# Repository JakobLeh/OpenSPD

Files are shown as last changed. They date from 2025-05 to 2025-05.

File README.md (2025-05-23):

# OpenSPD

**OpenSPD** (Open-Source Single Photon Detector) is a hardware project for detecting single photons in the near-infrared (NIR) range, specifically designed for applications such as photonic side-channel analysis using hot-carrier luminescence (HCL) from integrated circuits. The project is centered around a compact, low-cost, and high-sensitivity InGaAs avalanche photodiode (APD).

This repository contains the full open-source hardware files including:

- 🧩 **KiCad project files** (schematics, layout)
- 📦 **Bill of Materials (BOM)**
- 📚 **Custom libraries**
- 🧾 Supporting documentation

## Features

- **Avalanche Photodiode (APD)**: Excelitas C30645L-080 for high NIR sensitivity.
- **Bias Supply**: Adjustable high-voltage bias using MAX1932 DC-DC converter.
- **Transimpedance Amplifier (TIA)**: High-speed current-to-voltage conversion using the AD8015.
- **Gate Input**: Supports (sinusoidal, square-wave) gated operation for time-selective photon detection.
- **Passive Quenching**: Simple passive quenching resistor for avalanche suppression.
- **Mechanical Mounting Interface**: Compatible with free-space optical setups

### Front Side

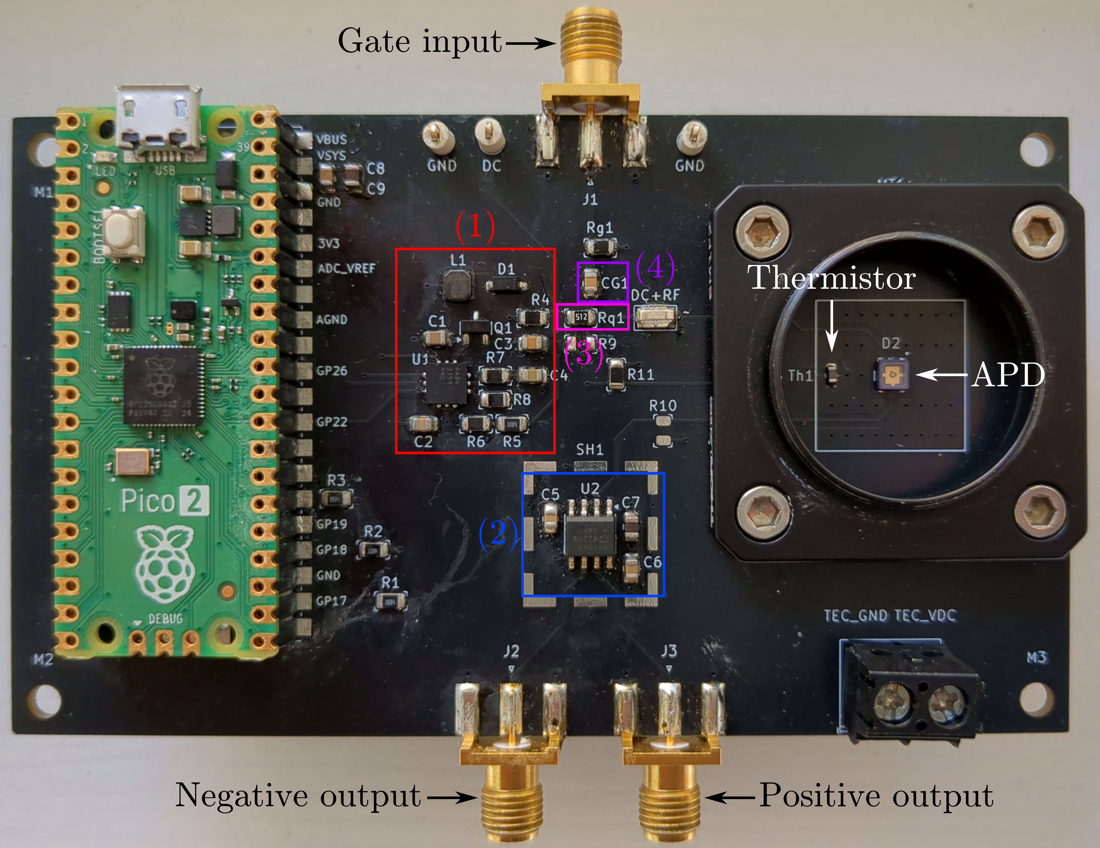
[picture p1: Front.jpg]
OpenSPD Front Side


### Back Side

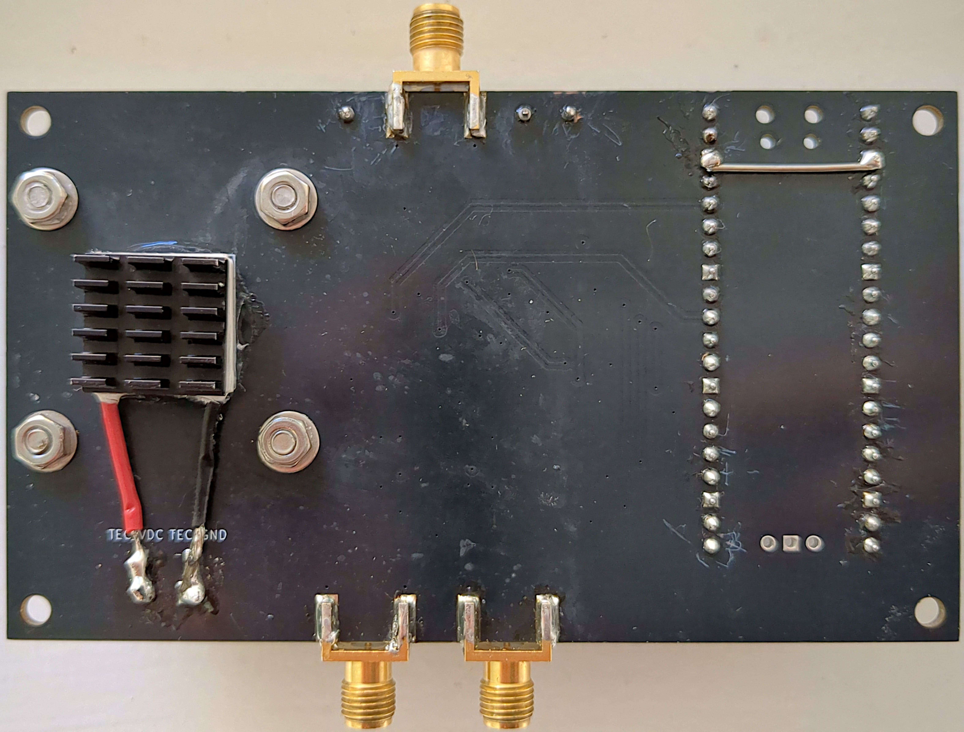
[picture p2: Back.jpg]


Date: May 2025

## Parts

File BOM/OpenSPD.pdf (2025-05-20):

OpenSPD

Reference | Value | Qty | DigiKey Part Number | Price (€)
C1 | 1µ | 1
C2 | 0.047µ | 1
C3,C5,C6,C8 | 0.1µ | 4
C4 | 0.22µ | 1
C7,C9 | 10µ | 2
CG1 | 10n | 1
D1 | BAT46W-E3-08 | 1 | BAT46W-E3-08CT-ND | 0.42
D2 | C30645L-080 | 1 | 1601-C30645L-080-ND | 71.64
J1,J2,J3 | Conn_Coaxial | 3 | 900-0732511153-ND | 9.75
J4 | Screw_Terminal_01x02 | 1 | 277-16667-ND | 0.61
L1 | 100µ | 1 | 553-3303-2-ND | 0.25
Q1 | BSS123 | 1 | BSS123NCT-ND | 0.33
R1,R2,R3,R5 | 1M | 4
R4 | 806 | 1
R6 | 24.9k | 1
R7 | 20k | 1
R8 | 32.4k | 1
R9 | 91k | 1
R10,Rg1 | 49.9 | 2
R11,Rq1 | 10k | 2
Th1 | 10k | 1 | 445-2554-2-ND | 0.17
TP1,TP2,TP3 | 5002 | 3 | 36-5002-ND | 1.02
TP4 | 5019 | 1 | 36-5019CT-ND | 0.33
U1 | MAX1932 | 1 | MAX1932ETC+TCT-ND | 13.17
U2 | AD8015 | 1 | 505-AD8015ARZ-ND | 11.74
U3 | Pi Pico 2 | 1 | 2648-SC1631CT-ND | 4.40
- | TEC | 1 | 102-4432-ND | 15.52
- | Heat Sink | 1 ATS015015006-PF-4E-ND | 4.07
Thorlabs: | SM1F2 | 1 | | 23.57
- | SM1V10 | 1 | | 35.25
- | SM1L10 | 1 | | 14.99
- | LA4052-C | 1 | | 128.26
| | | Without Thorlabs | = 133.42 €
| | | Everything | = 335.49 €

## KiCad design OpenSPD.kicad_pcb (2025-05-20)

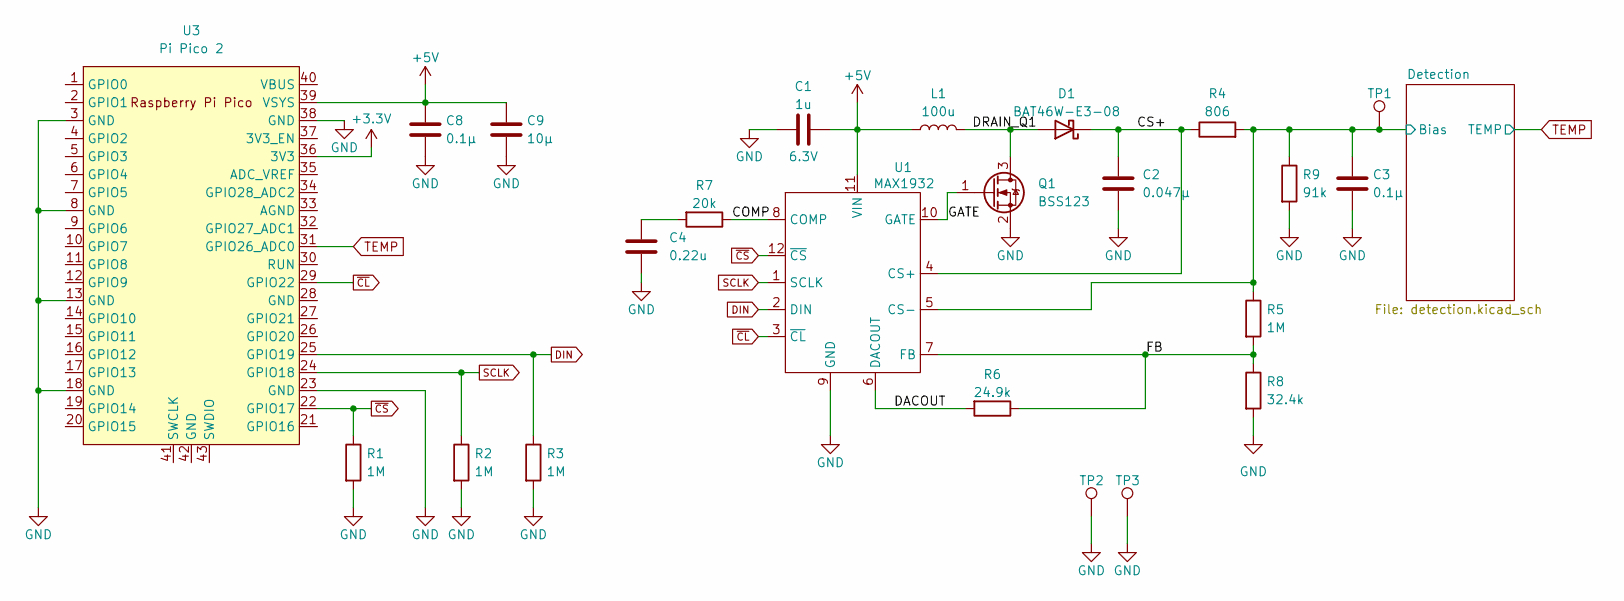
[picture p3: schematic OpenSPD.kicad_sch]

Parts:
C1: 1u; C_0805_2012Metric; Voltage 6.3V
C2: 0.047µ; C_0805_2012Metric
C3, C8: 0.1µ; C_0805_2012Metric
C4: 0.22u; C_0805_2012Metric
C9: 10µ; C_0805_2012Metric
D1: BAT46W-E3-08; SOD-123; DigiKey Part Number BAT46W-E3-08TR-ND
L1: 100u; 100µ_L
Q1: BSS123; SOT-23; DigiKey Part Number BSS123NTR-ND
R1, R2, R3, R5: 1M; 0805_2012_Vishay
R4: 806; 0805_2012_Vishay
R6: 24.9k; 0805_2012_Vishay
R7: 20k; 0805_2012_Vishay
R8: 32.4k; 0805_2012_Vishay
R9: 91k; 0805_2012_Vishay
TP1, TP2, TP3: TestPoint; TestPoint_Keystone_5002; DigiKey Part Number 445-2554-2-ND
U1: MAX1932; T1244-4; DigiKey Part Number MAX1932ETC+TTR-ND
U3: Pi Pico 2; RPi_Pico_SMD_TH

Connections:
+3.3V: U3.36 (3V3); also elsewhere on the board
+5V: C1.2, C8.1, C9.1, L1.1, U1.11 (VIN), U3.39 (VSYS); also elsewhere on the board
/COMP: R7.1, U1.8 (COMP)
/CS+: C2.1, D1.1 (K), R4.1, U1.4 (CS+)
/DACOUT: R6.2, U1.6 (DACOUT)
/DRAIN_Q1: D1.2 (A), L1.2, Q1.3 (D)
/Detection/Bias: C3.1, R4.2, R5.1, R9.1, TP1.1, U1.5 (CS-); also elsewhere on the board
/FB: R5.2, R6.1, R8.1, U1.7 (FB)
/GATE: Q1.1 (G), U1.10 (GATE)
DIN: R3.1, U1.2 (DIN), U3.25 (GPIO19)
GND: C1.1, C2.2, C3.2, C4.2, C8.2, C9.2, Q1.2 (S), R1.2, R2.2, R3.2, R8.2, R9.2, TP2.1, TP3.1, U1.9 (GND), U3.3 (GND), U3.8 (GND), U3.13 (GND), U3.18 (GND), U3.23 (GND), U3.38 (GND); also elsewhere on the board
unnamed: C4.1, R7.2
SCLK: R2.1, U1.1 (SCLK), U3.24 (GPIO18)
TEMP: U3.31 (GPIO26_ADC0); also elsewhere on the board
~CL: U1.3 (~CL), U3.29 (GPIO22)
~CS: R1.1, U1.12 (~CS), U3.22 (GPIO17)

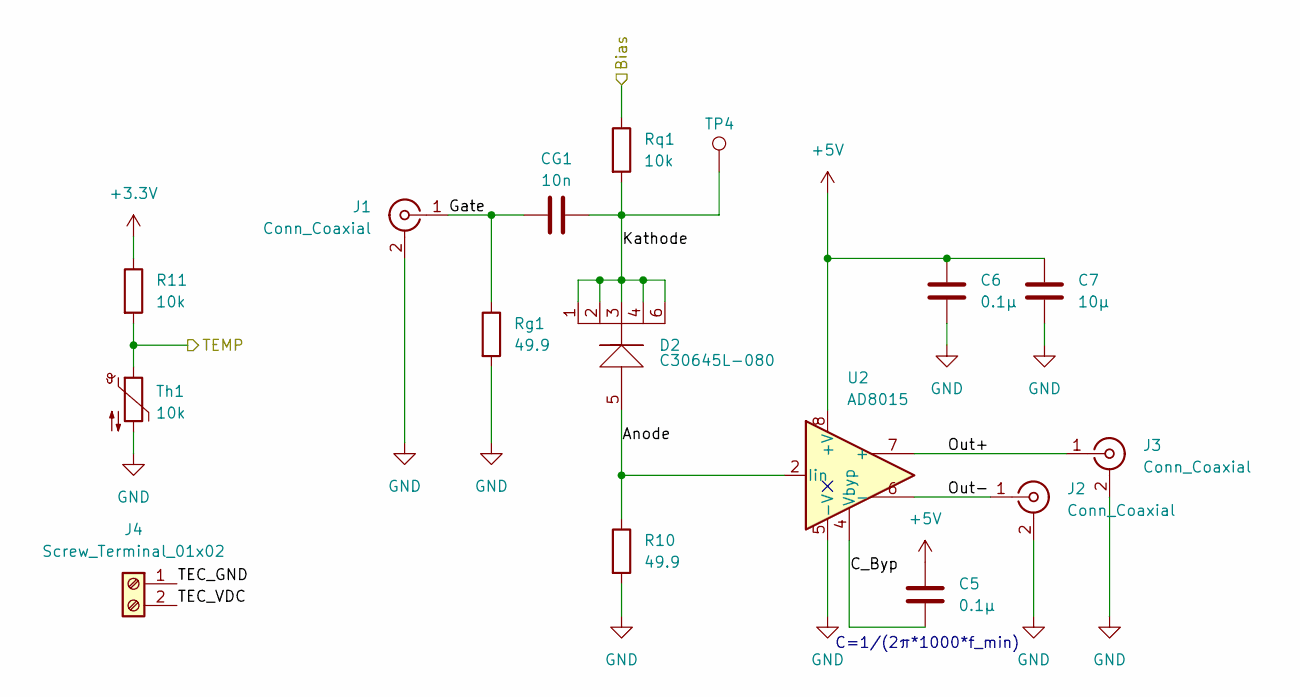
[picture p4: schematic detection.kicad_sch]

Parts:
C5, C6: 0.1µ; C_0805_2012Metric
C7: 10µ; C_0805_2012Metric
CG1: 10n; C_0805_2012Metric
D2: C30645L-080; DigiKey Part Number 1601-C30645L-080-ND
J1, J2, J3: Conn_Coaxial; SMA_Molex_73251-1153_EdgeMount_Horizontal; DigiKey Part Number 900-0732511153-ND
J4: Screw_Terminal_01x02; TerminalBlock_Phoenix_PT-1,5-2-5.0-H_1x02_P5.00mm_Horizontal; DigiKey Part Number 277-16667-ND
R10: 49.9; 0805_2012_Vishay
R11: 10k; 0805_2012_Vishay
Rg1: 49.9; 0805_2012_Vishay
Rq1: 10k; 0805_2012_Vishay
TP4: TestPoint; TestPoint_Keystone_5019_Minature; DigiKey Part Number 36-5019TR-ND
Th1: 10k; R_0603_1608Metric
U2: AD8015; SOIC-8_3.9x4.9mm_P1.27mm; DigiKey Part Number 505-AD8015ARZ-ND

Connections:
+3.3V: R11.1; also elsewhere on the board
+5V: C5.1, C6.1, C7.1, U2.8 (+V); also elsewhere on the board
/Detection/Anode: D2.5, R10.1, U2.2 (Iin)
/Detection/Bias: Rq1.1; also elsewhere on the board
/Detection/C_Byp: C5.2, U2.4 (Vbyp)
/Detection/Gate: CG1.1, J1.1 (In), Rg1.1
/Detection/Kathode: CG1.2, D2.1, D2.2, D2.3, D2.4, D2.6, Rq1.2, TP4.1
/Detection/Out+: J3.1 (In), U2.7 (+)
/Detection/Out-: J2.1 (In), U2.6 (-)
/Detection/TEC_GND: J4.1; also elsewhere on the board
/Detection/TEC_VDC: J4.2; also elsewhere on the board
GND: C6.2, C7.2, J1.2 (Ext), J2.2 (Ext), J3.2 (Ext), R10.2, Rg1.2, Th1.2, U2.5 (-V); also elsewhere on the board
TEMP: R11.2, Th1.1; also elsewhere on the board

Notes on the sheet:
C=1/(2π*1000*f_min)

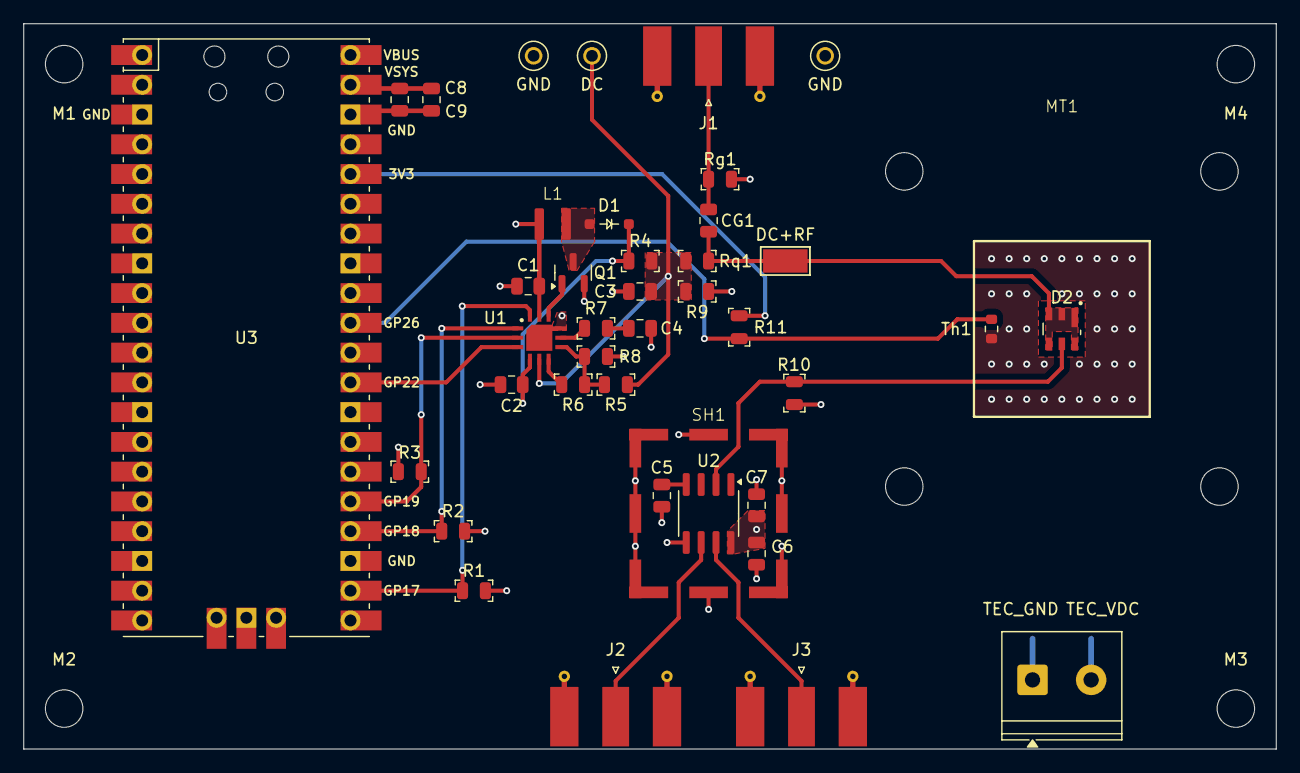
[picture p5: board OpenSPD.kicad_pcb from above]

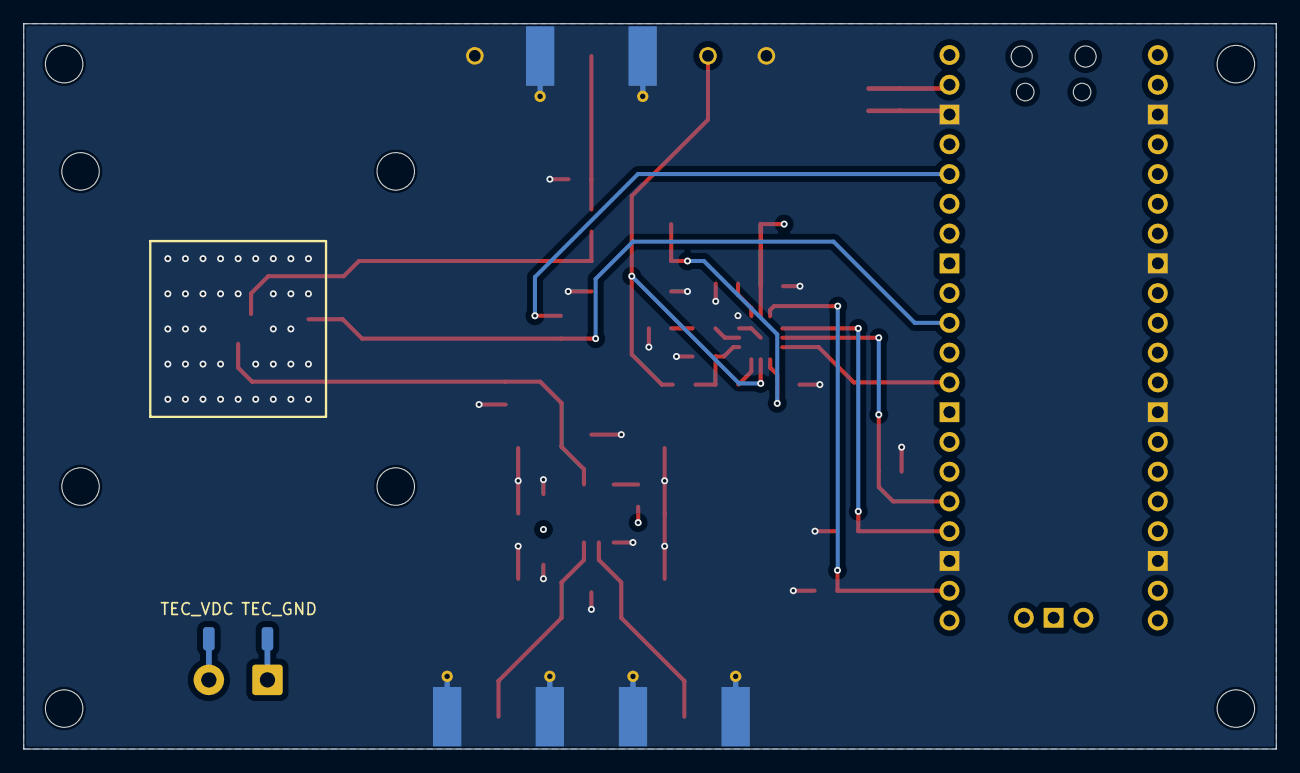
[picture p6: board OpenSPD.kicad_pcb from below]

Board: 4 copper layers, 106.9 x 61.9 mm, 47 parts (2 on the bottom side), 24 nets.

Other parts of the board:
M1, M2, M3, M4: MountingHole_3.2mm_M3
MT1: SM1F2
SH1: Shield_3610213126S
TEC_GND: SolderWirePad_1x01_SMD_1x2mm
TEC_VDC: SolderWirePad_1x01_SMD_1x2mm

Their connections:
/Detection/TEC_GND: TEC_GND.1; also elsewhere on the board
/Detection/TEC_VDC: TEC_VDC.1; also elsewhere on the board
GND: SH1.1; also elsewhere on the board
